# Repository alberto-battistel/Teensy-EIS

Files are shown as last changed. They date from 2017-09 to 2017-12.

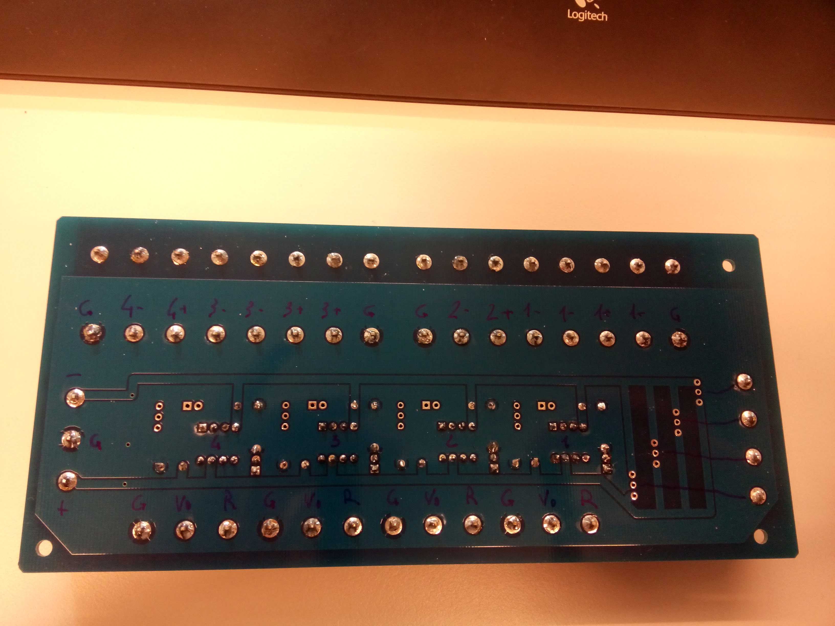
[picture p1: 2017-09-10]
analog front-end/4Input-1Output_board/srDescription_Figures/Board_Backside.jpg

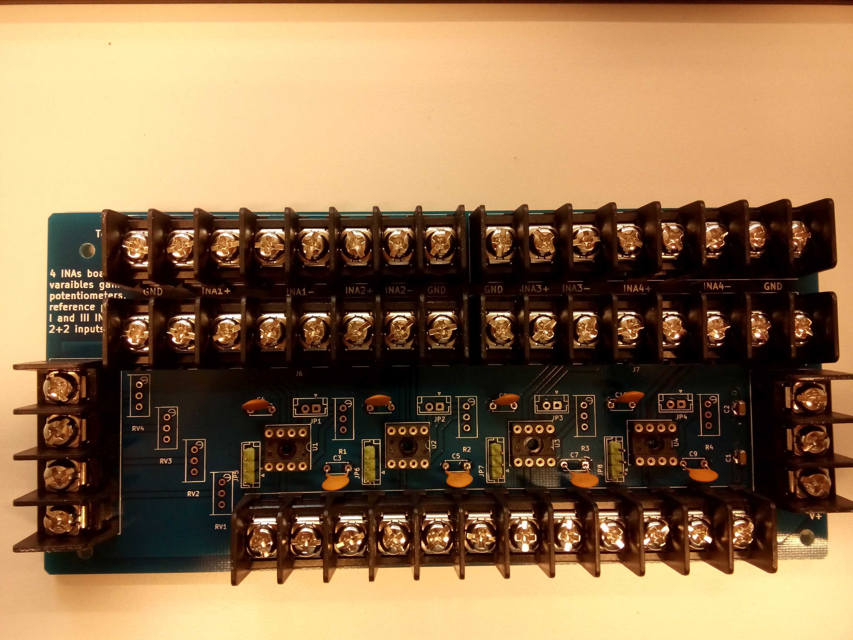
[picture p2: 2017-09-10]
analog front-end/4Input-1Output_board/srDescription_Figures/Board_Frontside.jpg

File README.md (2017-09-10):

# Teensy-EIS

At the moment this git is still slightly chaotic, but it is getting better.
The idea is to use the two ADCs of the Teensy 3.6 (pjrc.com) to aquire data and the DAC to create the perturbation (sinus/multisine) to work as an impedance analyzer. All controlled by a PC using Python, which also make the analysis part. We have an analog front-end for voltage shift (Teensy works 0-3.3V both ADC and DAC) to connect to the real potentiostat. This is tested and works.

## 1 - ADC-DAC
ADC-DAC.ino and readFromPython.py work together. They are THE Teensy-EIS programs. CalculateParameters.m helps to make the parameters to feed in Python.

## 2 - Examples
In ADC-DAC there are examples of the part of the ADC-DAC.ino. DAC is for the DAC and PingPong manages the serial communication with the PC. They are more or less the most updated or the same as in ADC-DAC.ino.

## 3 - Regarding the DAC
The signal for the DAC is generated through a Matlab/GNU Octave/Scilab script. (Generate_DAC_vector). 

## 4 - Analog front-end
In analog front-end there is all about the core of the voltage shift. All the analog interface with the instrument is based on four INA128. They are very flexible pieces. There is no schematic for the power stage and activation of the signal line, but the elements are in the two PDF.

## 5 - Control flow
In Schematics there are the diagrams of the programs. At the moment only the part for the aquisition, which is the most complex. In summary, the Teensy can aquire infinite amount of data which are streamed in blocks to the PC. Python can handle easily several milions data points. 

## 6 - pointer?
pointers-reference-test contains a couple of examples about passing by reference or by pointer to a function. Not fundamental for the rest, just to remember.

------------------------------------
# Version list:

## Version 1.00
Fully operational tidy up version.

## Version 0.99
Fully operational prototype, both for the programing side and for the analog side. 

------------------------------------
# Bug List:
So we can keep track of what needs to be fixed

-To be filled (Priority: 1)

------------------------------------
# Future Feature List:

## Version 1.1?
what shall we implement next?

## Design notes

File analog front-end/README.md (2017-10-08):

# Analog front-end
The analog front-end interfaces the *Teensy* to the instrument (potentiostat). It serves as conditioning of the signals. It mainly provides low impedance for the inputs, level shift (*Teensy* is 0-3.3V), and some degree of rejection for ground loops (still to understand a bit better). It also features an independent power stage (USB compatible) to handle bipolar signals.

## Signal conditioning
At the moment the conditioning is build on 4 **INAs 128** (Instrumentation amplifiers) from Texas Instruments. They are flexible building blocks featuring low noise, low distortion, easy level shift, and high impedance inputs (10 GOhm). Two INAs are used to buffer, level shift, and shrink the DAC (digital to analog converter) of the *Teensy* and the other two are for level shifting of the inputs of the two ADCs (analog to digital converter). 
Analog filtering can be easily attached to the INAs.
**4Input-1Output_board** contains the full design (schematics and printed circuit board layout with bill of components) to build up the signal conditioning part. It is a very flexible board. We also employ it for *additional reference electrode probes* in electrochemical cells or to *break groud loops*.

## Power
The power stage is based on a **DC-DC converter** (*NMA0515SC* from Murata). It takes 5 V as input and provides +/- 15 V. It may be connected to the *Teensy* and take power from the same USB cable, but we did not test this yet. The bipolar voltage is used to power the INAs. The positive rail is also used to hold a normally open **signal relay** (*MT2 Relay* from AXICOM). This relay is controlled by a digital pin of the *Teensy* through a transistor (*2N3904*) and it is necessary to cut the DAC line from the *Teensy* toward the instrument so that unwanted signals cannot be injected (for example when you turn on the *Teensy*...).

## State of the material
At the moment the schematics and the PCB layout signal conditioning part is available in **4Input-1Output_board**, but we may come out with a more practical design later. 
**Complete_analog_front-end.pro** (*KiCAD project* in **Design_schematics**) contains the *functional design* of the project with the fundamental connections between the *Teensy* and the analog front-end and the power stage.

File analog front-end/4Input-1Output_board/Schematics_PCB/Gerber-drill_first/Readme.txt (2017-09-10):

Contact:
Alberto Battistel

Email:
alberto.battistel@epfl.ch

Address:
EPFL Valais Wallis
Laboratoire d’Electrochimie Physique et Analytique (LEPA)
Rue de l'Industrie 17
Case Postale 440
CH-1951 Sion

updated version: 6 February 2017

features
board with 2 copper layer
dimensions: 182.86 mm * 83.82 mm
silkscreen only on top
soldermask on top and bottom

filenames

top silkscreen: schematic3-F.SilkS

top soldermask: schematic3-F.Mask

top copper: schematic3-F.Cu

bottom copper: schematic3-B.Cu

bottom soldermask: schematic3-B.Mask

board outline: schematic3-Edge.Cuts

NC Drill: schematic3.drl

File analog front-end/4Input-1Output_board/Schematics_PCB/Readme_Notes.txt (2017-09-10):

First manufactoring 
6 Feb 2017

Problems:

1- rong footprint for the two 10 uF capacitors. It is possible to solder them but it is annoying.
2- Errors in some writings: board description, INAs inputs.

24 Feb 2017

Corrected:
1- correction of board description and INAs inputs.

To do:
correct footprint of 10 uF capacitors.

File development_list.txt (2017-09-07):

#List of things to implement

## Add license

## Loop microcontroller
activate DAC2 for voltage shift
make functions in the sketch
loop the aquisition for listening from the PC

## Loop python control
Send parameters (Pingpong script)
make analysis (FFT)

## Analog front-end
for DAC (voltage divider, voltage shift, activation relay)
for ADC (voltage shift)
transistor to drive the relay from the Teensy
additional transistors for 5V communication (trigger instrument)

## Real experiment
digital test (impendance DAC vs 2*ADC) to see resolution, linearity
real analog experiment interfaced with a potentiostat

## Future staff
Raspberry PI
portable potentiostat
different experiments (CV, battery cycles)
GUI

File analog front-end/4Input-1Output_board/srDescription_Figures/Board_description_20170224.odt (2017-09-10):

4 INAs board

Alberto Battistel

24 February 2017

This board contains is made to allocate 4 INAs and 4 variable voltage dividers. INA 1 and 3 have two screw terminals for every inputs. INA 2 and 4 have only one screw terminal for input.

Signal inputs Signaloutputs Voltage dividers Power
Figure 1: Top view of the board.

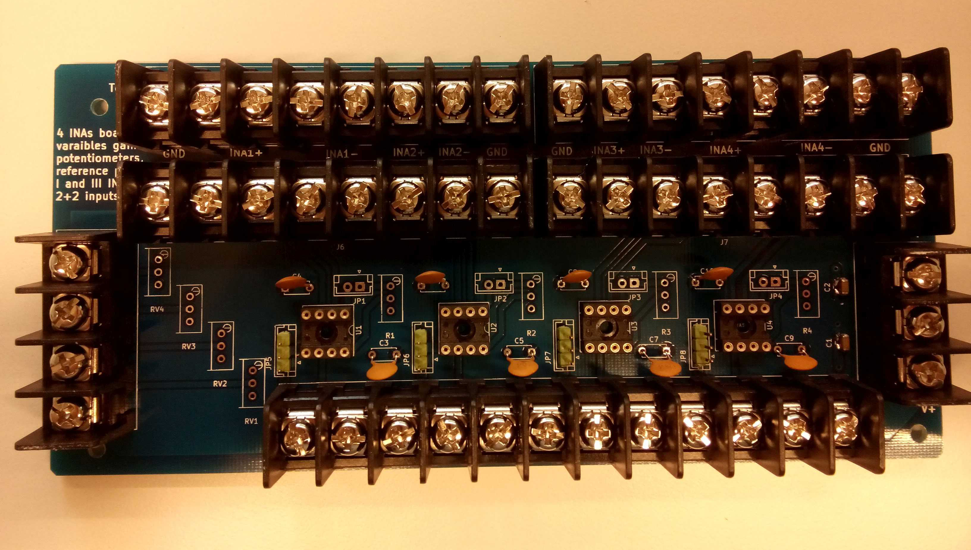
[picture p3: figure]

Note that there are some errors on the labels of the inputs. The backside (Figure 2) has the right labels.

The double terminal row on the signal inputs can be used for filtering and summing.

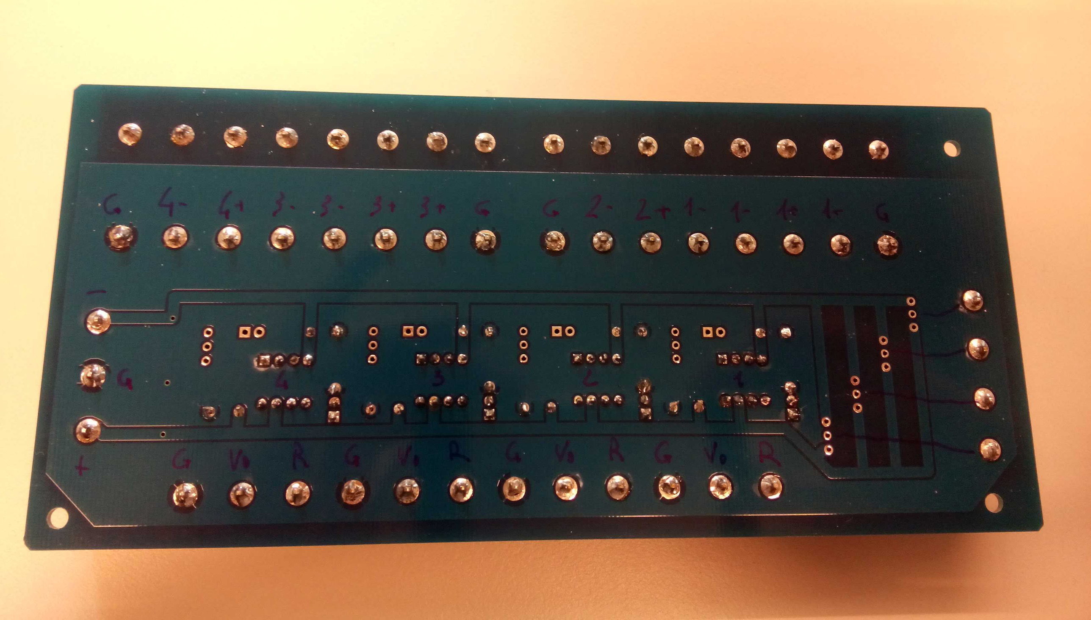
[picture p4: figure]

Figure 2: back side of the board with right labels

Label | Description
G | Ground
R | External reference potential
Vo | INA output
+ | Positive rail
− | Negative rail
n+ | Positive input INA n
n− | Negative input INA n

Table 1: labels on the board.

INAOn the board is possible to change the gain factor through a variable resistance and select if the INA works against ground or against a provided reference voltage.

Variable resistor for gain Jumper for gain Jumper for external Reference potential Refer to ground Refer to external reference
Figure 3: single INA block with jumpers for gain and reference potential.

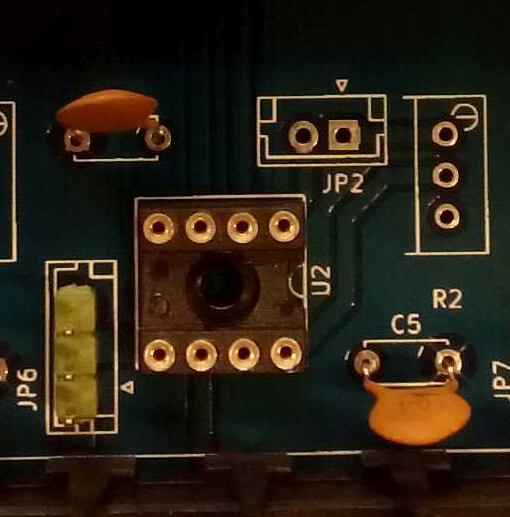
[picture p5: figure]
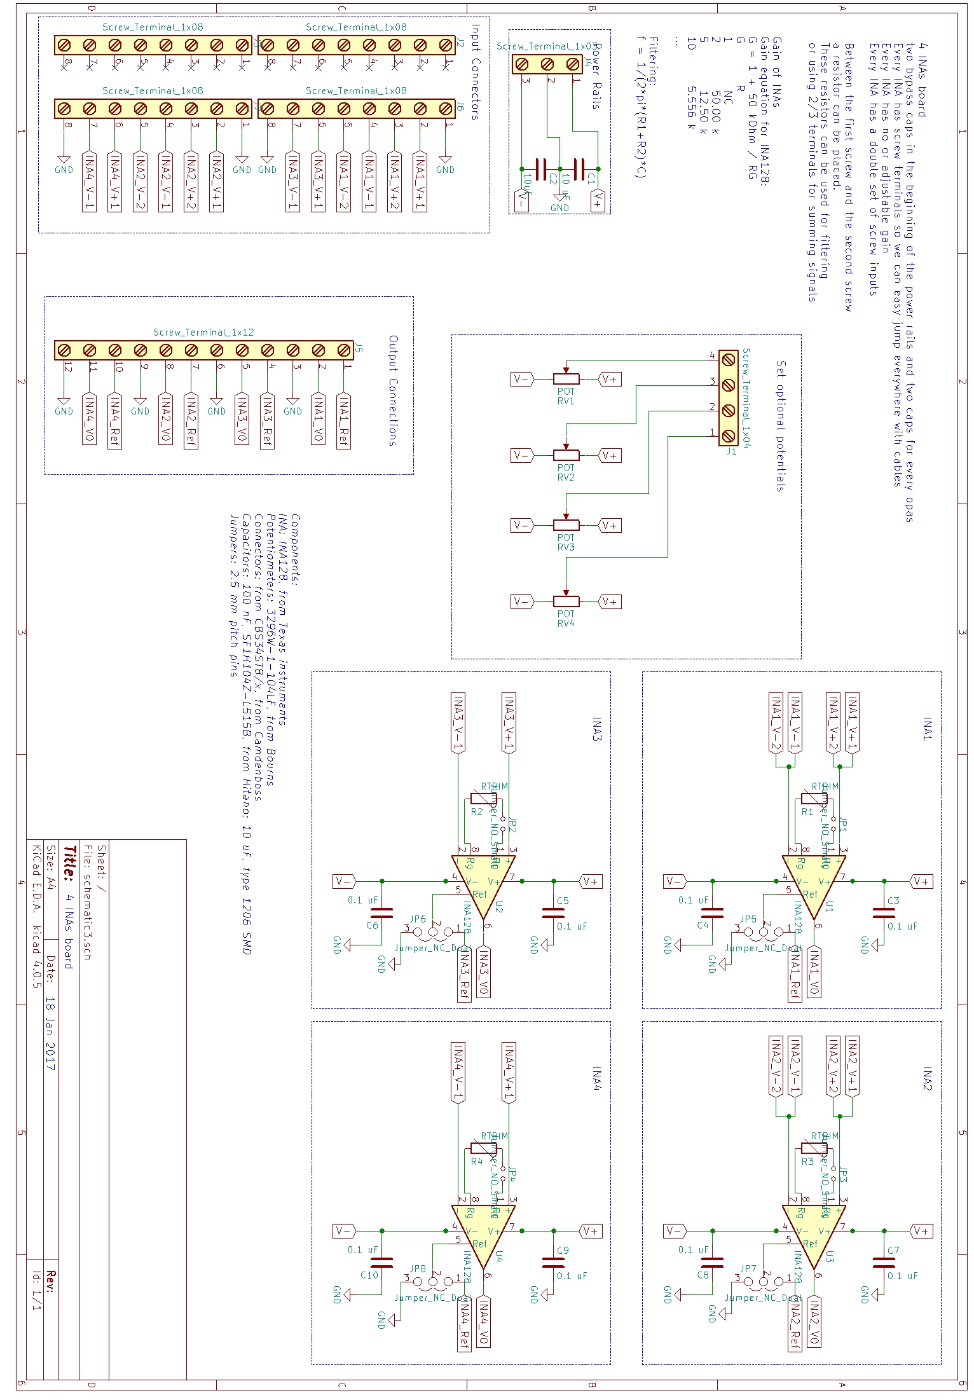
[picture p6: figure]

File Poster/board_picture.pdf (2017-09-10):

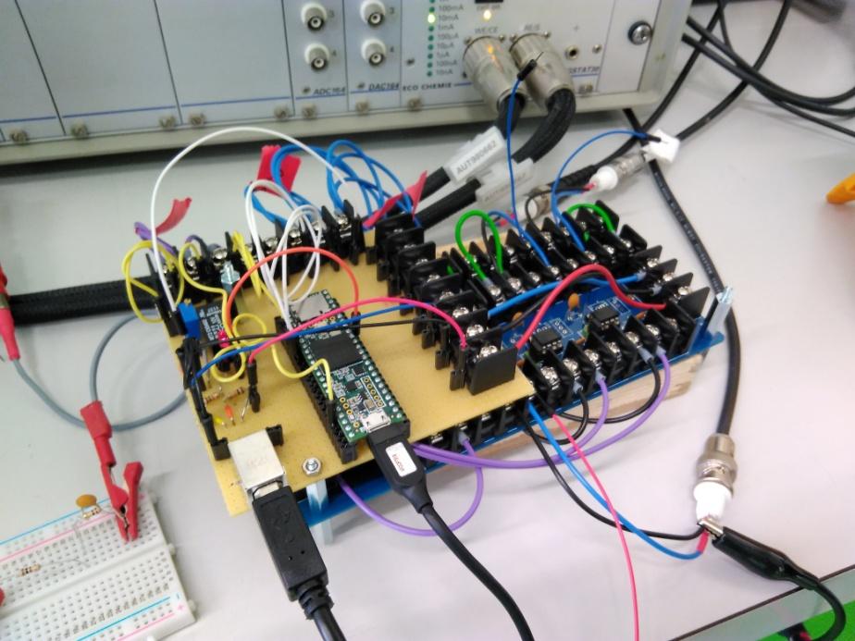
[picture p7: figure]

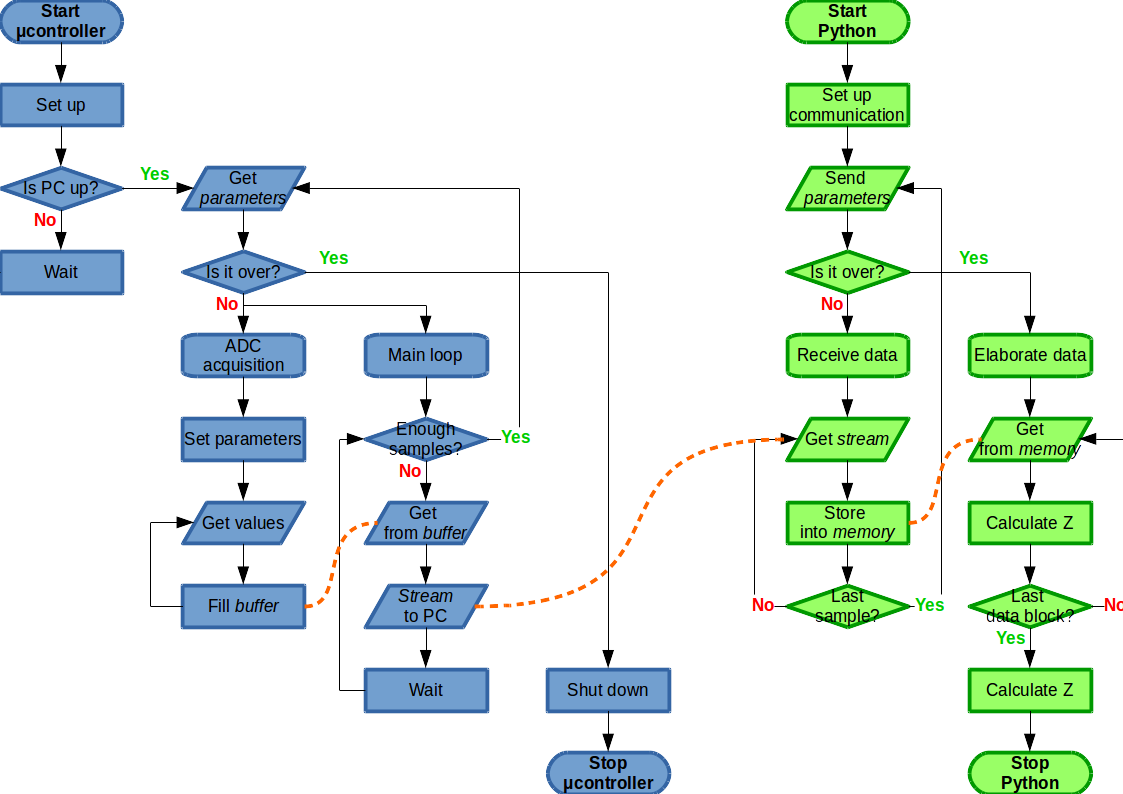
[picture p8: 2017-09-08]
Schematics/FlowChartProgram.png

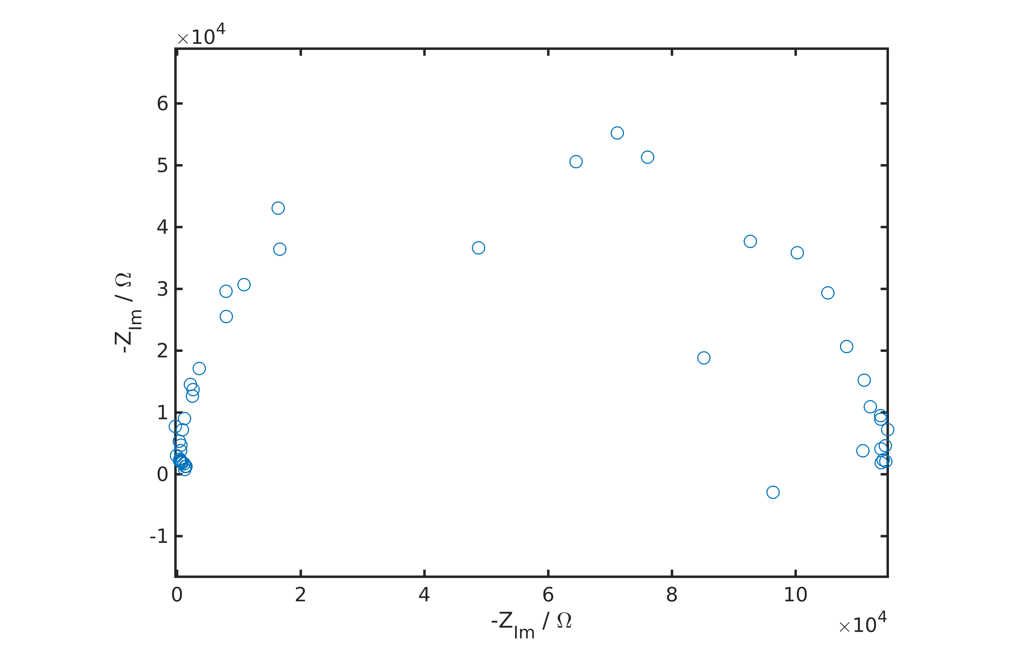
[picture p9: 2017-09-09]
Poster/GoodNyquist.png

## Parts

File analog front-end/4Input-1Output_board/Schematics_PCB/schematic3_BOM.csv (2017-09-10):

Id | Designator | Package | Quantity | Designation | Supplier and ref
1 | J7,J6,J3,J2 | Camdenboss_Screw_terminal_8x9.5mm | 4 | Screw_Terminal_1x08
2 | J4 | Camdenboss_Screw_terminal_3x9.5mm | 1 | Screw_Terminal_1x03
3 | C1 | C_0603_HandSoldering | 1 | 10 uF
4 | C2 | C_0603_HandSoldering | 1 | 10uF
5 | U1,U2,U3,U4 | DIP-8_W7.62mm_Socket | 4 | INA128
6 | J5 | Camdenboss_Screw_terminal_12x9.5mm | 1 | Screw_Terminal_1x12
7 | J1 | Camdenboss_Screw_terminal_4x9.5mm | 1 | Screw_Terminal_1x04
8 | C3,C4,C5,C6,C7,C8,C9,C10 | C_Disc_D5.0mm_W2.5mm_P5.00mm | 8 | 0.1 uF
9 | R1,R2,R3,R4 | Potentiometer_Bourns_3296W_3-8Zoll_Inline_ScrewUp | 4 | RTRIM
10 | RV1,RV2,RV3,RV4 | Potentiometer_Bourns_3296W_3-8Zoll_Inline_ScrewUp | 4 | POT
11 | JP1,JP2,JP3,JP4 | JST_EH_B02B-EH-A_02x2.50mm_Straight | 4 | Jumper_NO_Small
12 | JP5,JP6,JP7,JP8 | JST_EH_B03B-EH-A_03x2.50mm_Straight | 4 | Jumper_NC_Dual

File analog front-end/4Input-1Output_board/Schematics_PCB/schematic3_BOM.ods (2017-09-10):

Id | Designator | Package | Quantity | Designation | Supplier and ref
1 | J7,J6,J3,J2 | Camdenboss_Screw_terminal_8x9.5mm | 4 | Screw_Terminal_1x08
2 | J4 | Camdenboss_Screw_terminal_3x9.5mm | 1 | Screw_Terminal_1x03
3 | C1 | C_0603_HandSoldering | 1 | 10 uF
4 | C2 | C_0603_HandSoldering | 1 | 10uF
5 | U1,U2,U3,U4 | DIP-8_W7.62mm_Socket | 4 | INA128
6 | J5 | Camdenboss_Screw_terminal_12x9.5mm | 1 | Screw_Terminal_1x12
7 | J1 | Camdenboss_Screw_terminal_4x9.5mm | 1 | Screw_Terminal_1x04
8 | C3,C4,C5,C6,C7,C8,C9,C10 | C_Disc_D5.0mm_W2.5mm_P5.00mm | 8 | 0.1 uF
9 | R1,R2,R3,R4 | Potentiometer_Bourns_3296W_3-8Zoll_Inline_ScrewUp | 4 | RTRIM
10 | RV1,RV2,RV3,RV4 | Potentiometer_Bourns_3296W_3-8Zoll_Inline_ScrewUp | 4 | POT
11 | JP1,JP2,JP3,JP4 | JST_EH_B02B-EH-A_02x2.50mm_Straight | 4 | Jumper_NO_Small
12 | JP5,JP6,JP7,JP8 | JST_EH_B03B-EH-A_03x2.50mm_Straight | 4 | Jumper_NC_Dual
 | Description | Reference | Distrelec Art.Nr. | Type | Price / CHF | Quantity | total cost / CHF
 | potentiometers | Potentiometer_Bourns_3296W_3-8Zoll_Inline_ScrewUp | 164-00-721 | 3296W-1-104LF | 1.9 | 20 | 38
 | screw terminals | Camdenboss_Screw_terminal_3x9.5mm | 148-31-248 | CBS34ST8/3 | 1.1 | 10 | 11
 |  | Camdenboss_Screw_terminal_4x9.5mm | 148-31-249 | CBS34ST8/4 | 1.52 | 10 | 15.2
 |  | Camdenboss_Screw_terminal_8x9.5mm | 148-31-254 | CBS34ST8/8 | 2.8 | 20 | 56
 |  | Camdenboss_Screw_terminal_12x9.5mm | 148-31-258 | CBS34ST8/12 | 3.75 | 10 | 37.5
 | capacitors | C_Disc_D5.0mm_W2.5mm_P5.00mm | 165-65-659 | SF1H104Z-L515B | 0.1044 | 100 | 10.44
 |  | C_0603_HandSoldering | 300-66-117 | RND 1501206X106K250 | 0.1004 | 20 | 2.008
 | pins |  |  |  |  |  | 0
 | jumpers | jumpers | 124-50-887 | CAB4GS | 0.136 | 50 | 6.8
 |  |  |  |  |  |  | 176.948
 | Description | Distrelec Art.Nr. | Type | Price / CHF | Quantity | total cost / CHF
 | potentiometers | 164-00-721 | 3296W-1-104LF | 1.9 | 20 | 38
 | screw terminals | 148-31-248 | CBS34ST8/3 | 1.1 | 10 | 11
 |  | 148-31-249 | CBS34ST8/4 | 1.52 | 10 | 15.2
 |  | 148-31-254 | CBS34ST8/8 | 2.8 | 20 | 56
 |  | 148-31-258 | CBS34ST8/12 | 3.75 | 10 | 37.5
 | capacitors | 165-65-659 | SF1H104Z-L515B | 0.1044 | 100 | 10.44
 |  | 300-66-117 | RND 1501206X106K250 | 0.1004 | 20 | 2.008
 | jumpers | 124-50-887 | CAB4GS | 0.136 | 50 | 6.8

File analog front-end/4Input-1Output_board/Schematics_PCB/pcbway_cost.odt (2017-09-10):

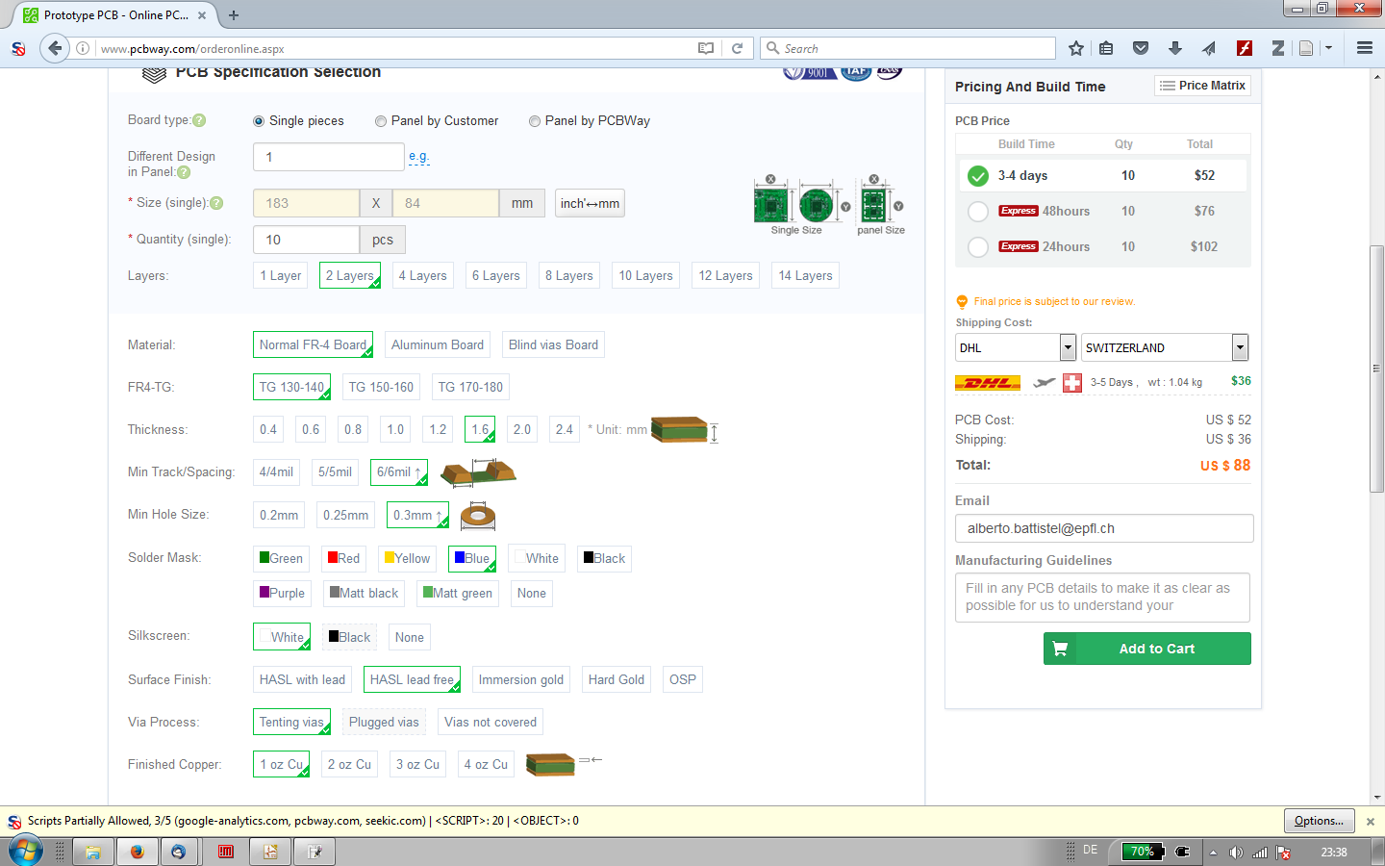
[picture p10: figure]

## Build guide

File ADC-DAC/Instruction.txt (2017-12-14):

every time you shutdown Teensy (exit(0)), you need to press the botton on the Teensy.

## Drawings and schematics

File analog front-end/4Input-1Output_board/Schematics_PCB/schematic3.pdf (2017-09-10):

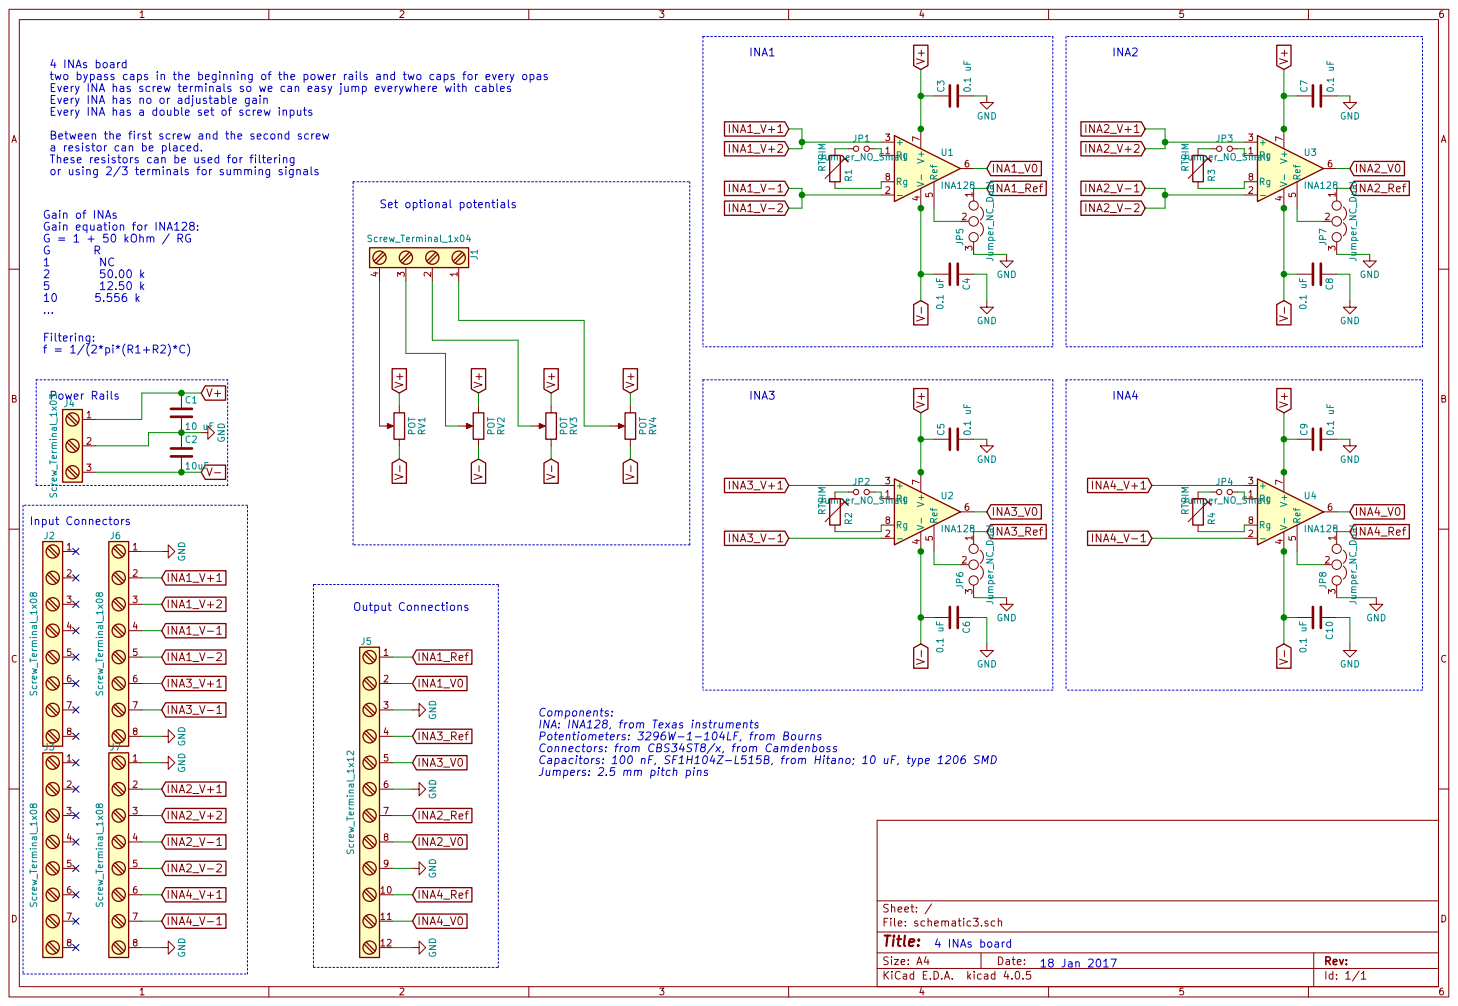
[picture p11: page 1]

4 INAs board
two bypass caps in the beginning of the power rails and two caps for every opas
Every INA has screw terminals so we can easy jump everywhere with cables
Every INA has no or adjustable gain
Every INA has a double set of screw inputs Between the first screw and the second screw

These resistors can be used for filtering

a resistor can be placed.

J5 Screw_Terminal_1x12
INA4_V0 GND GND GND GND

INA: INA128, from Texas instruments
Potentiometers: 3296W-1-104LF, from Bourns
Connectors: from CBS34ST8/x, from Camdenboss
Capacitors: 100 nF, SF1H104Z-L515B, from Hitano; 10 uF, type 1206 SMD
Jumpers: 2.5 mm pitch pins

Id: 1/1 Title: File: schematic3.sch Sheet: /

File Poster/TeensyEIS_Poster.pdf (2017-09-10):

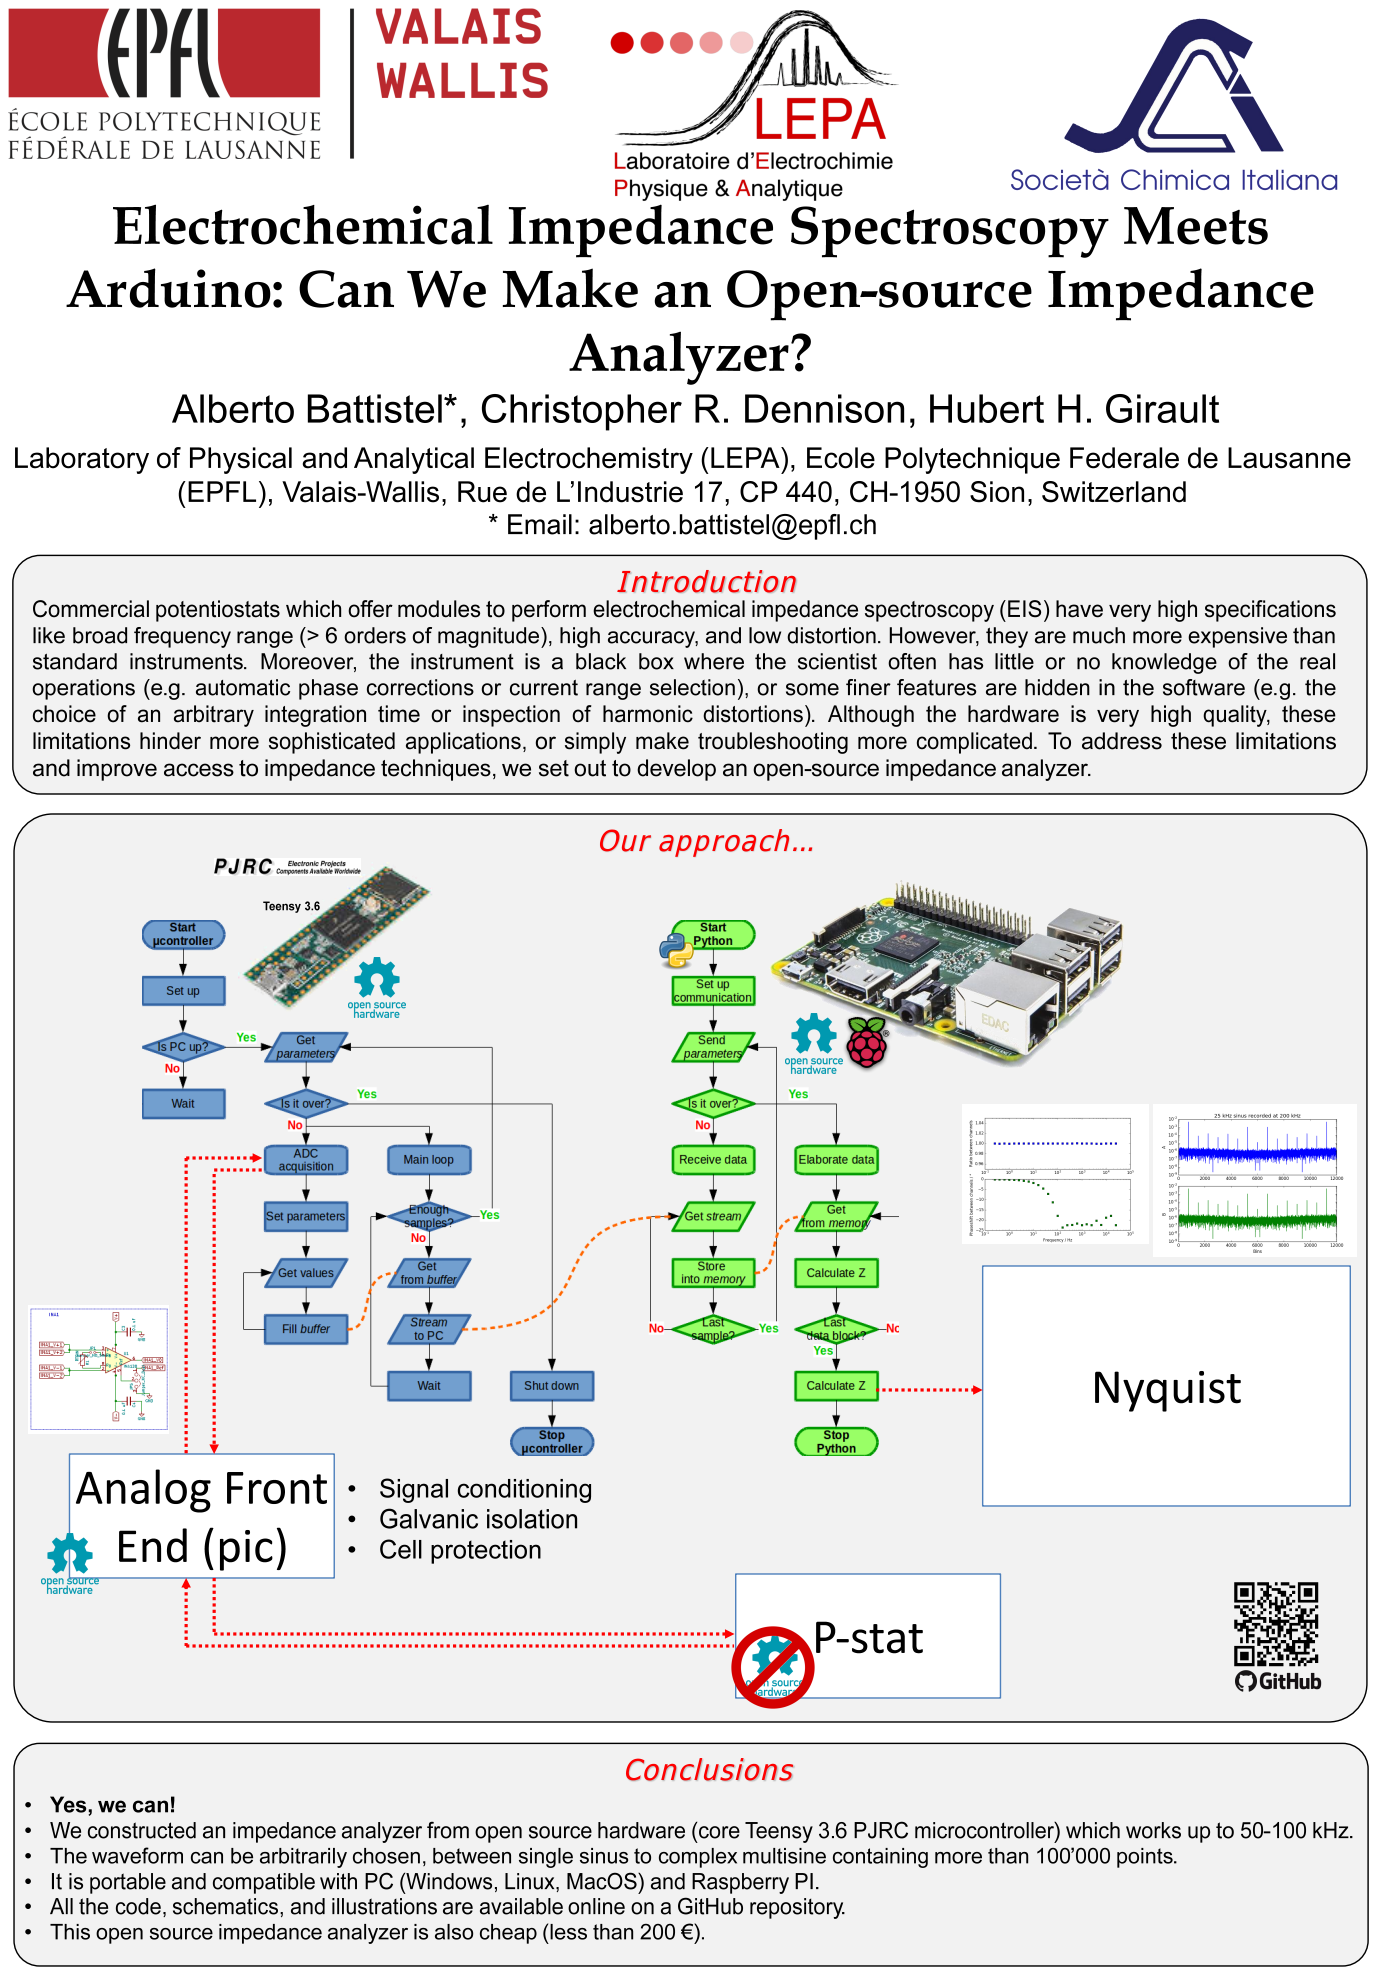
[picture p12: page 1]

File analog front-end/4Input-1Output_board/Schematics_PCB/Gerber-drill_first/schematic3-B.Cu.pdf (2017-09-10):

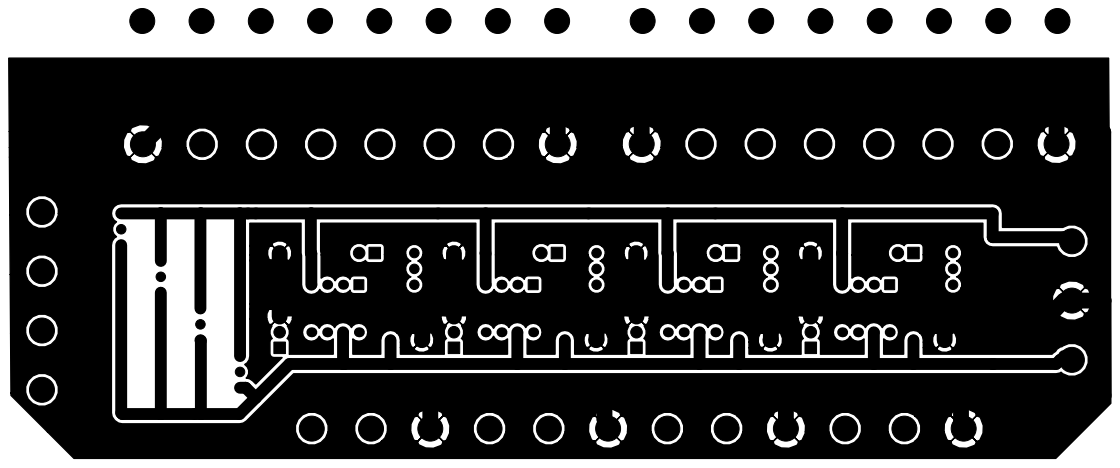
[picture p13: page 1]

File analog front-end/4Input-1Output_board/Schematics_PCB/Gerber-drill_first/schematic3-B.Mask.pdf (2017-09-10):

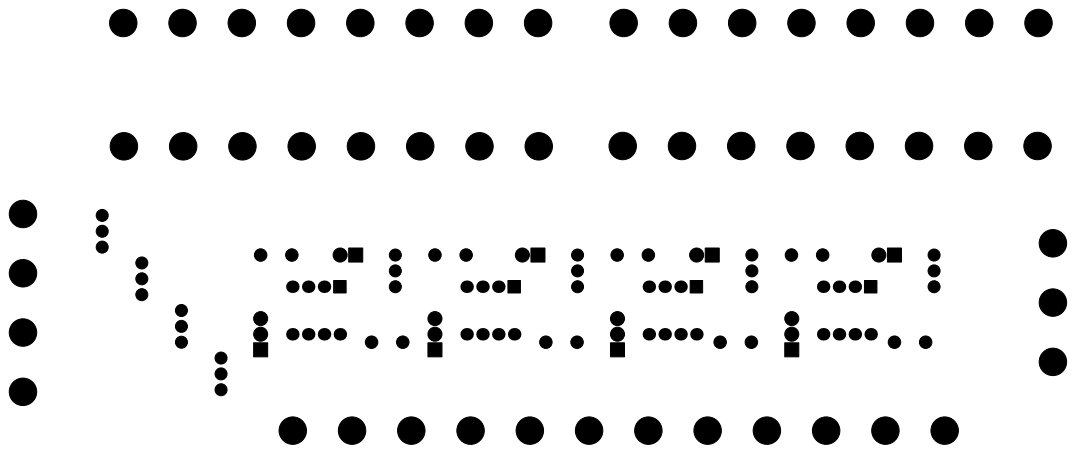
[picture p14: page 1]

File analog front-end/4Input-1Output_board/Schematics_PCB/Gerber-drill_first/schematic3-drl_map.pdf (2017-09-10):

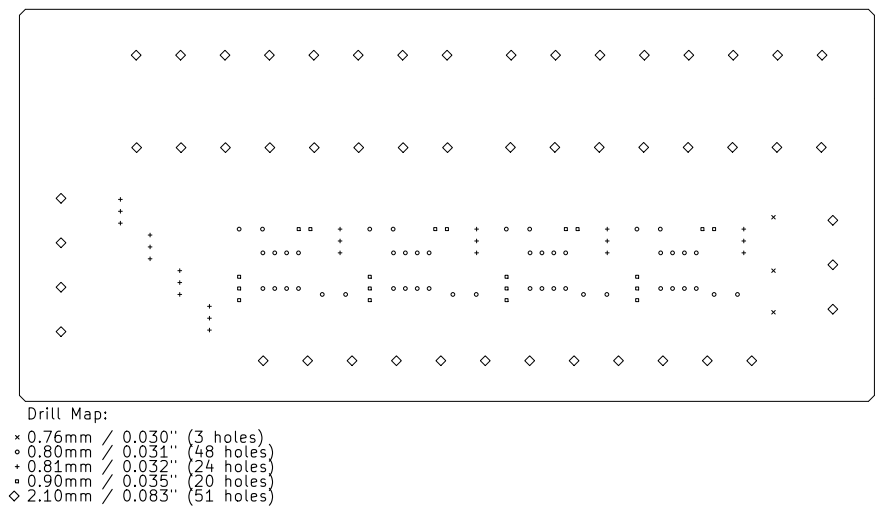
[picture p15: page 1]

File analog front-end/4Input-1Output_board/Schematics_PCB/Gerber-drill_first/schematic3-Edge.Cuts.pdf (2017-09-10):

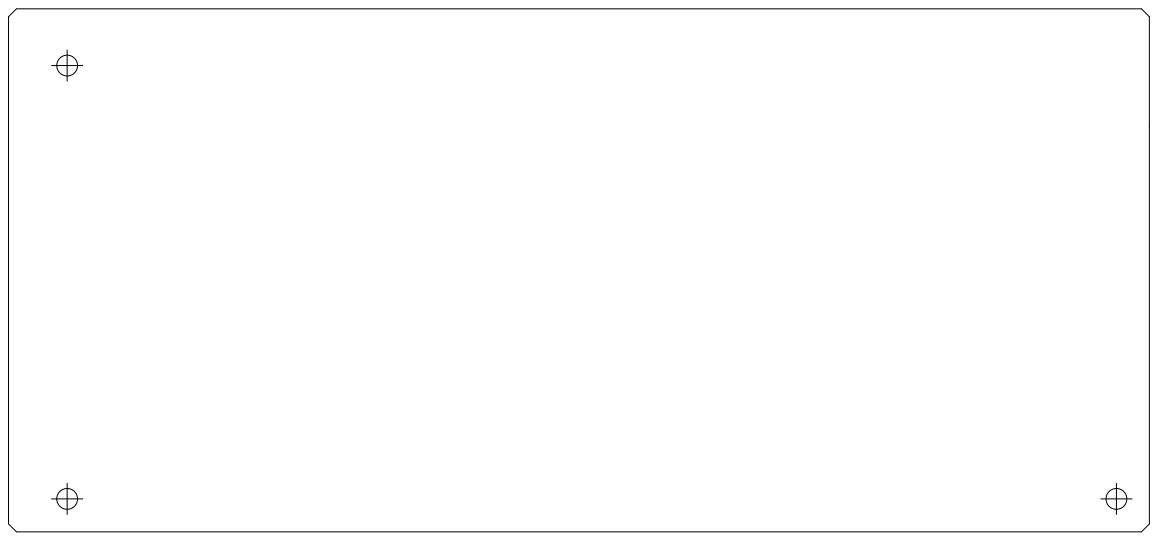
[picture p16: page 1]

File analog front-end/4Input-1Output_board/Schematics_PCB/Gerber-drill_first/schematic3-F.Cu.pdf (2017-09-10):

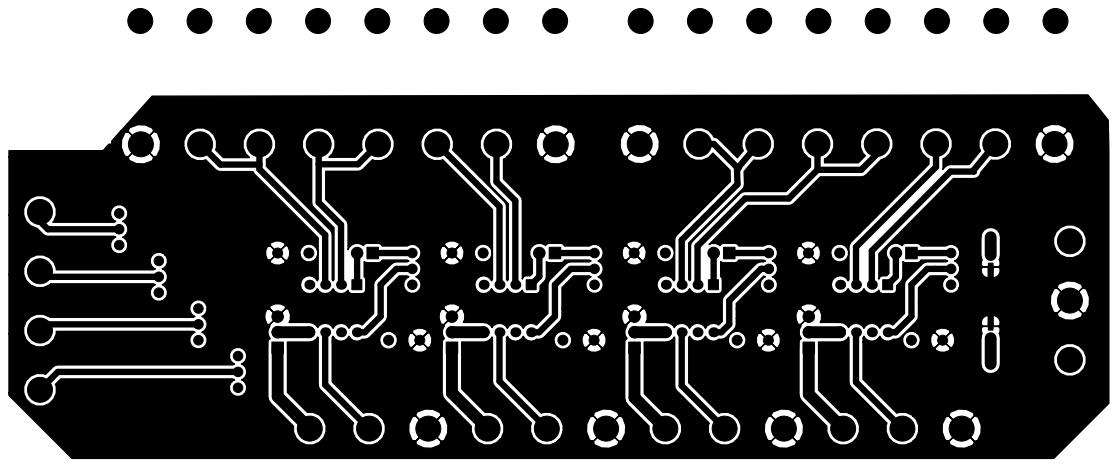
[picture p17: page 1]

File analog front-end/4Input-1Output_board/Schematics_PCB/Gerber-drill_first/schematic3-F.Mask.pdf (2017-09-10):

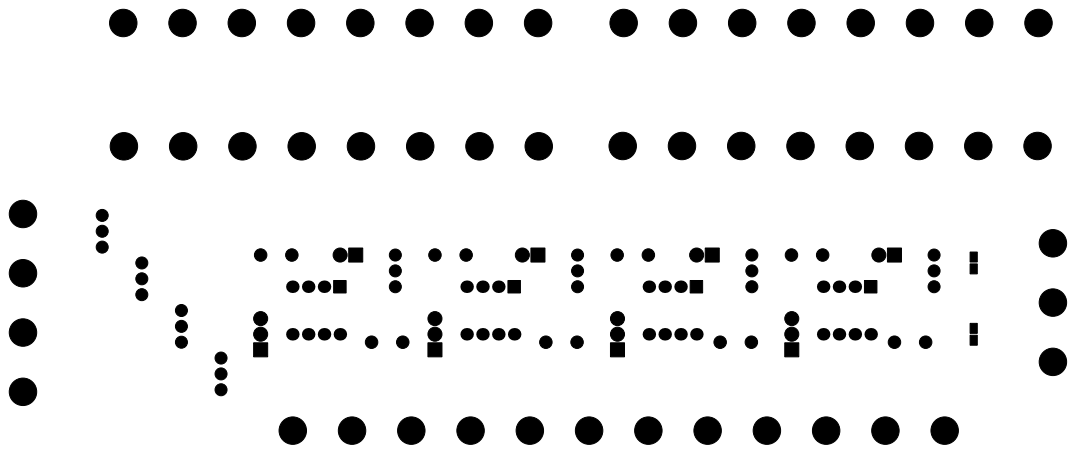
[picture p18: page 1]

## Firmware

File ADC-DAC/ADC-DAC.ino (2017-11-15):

#include <ADC.h>
#include <DMAChannel.h>
#include <array>
#include "DefaultParameters.h"
#include "DAC.h"


/* do you want to check timing?
 *  it print info about how many samples are collected per iteration
 *  and timing...
 */
//#define DEBUG

// ADC pins 
const uint8_t adc_pin0 = A9;  // digital pin 23, on ADC0
const uint8_t adc_pin1 = A19; // digital pin 31, on ADC1
// LED pin
const int ledPin = 13;
// Realy pin
const int RelayPin = 24;

// get parameters from the PC
#include "PingPong.h"   // contains function to get Parameters from Python

/* Count number of samples
 *  allow to stop the stream after collecting maxSamples
 */
bool stop4Samples[2] = {false, false};    // flag, signal that it streamed all the data of channels 0
uint32_t counterSamplesADC0 = 0;        // counter for data streamed for channel 0
uint32_t counterSamplesADC1 = 0;        // counter for data streamed for channel 1

/* Settings for Ring buffer (DMA)  */
// DMA buffer size
#define BUFFERSIZE 4096

// stream buffer size
uint16_t streamBuffer[2][BUFFERSIZE];

/* flags and counter */
// command to stop streaming
boolean streamData = true;

#ifdef DEBUG
// track in print time for serial print
unsigned long time_us = 0;
// count iterations
int16_t Iterations = 0;
#endif

// store index of DMA buffer
volatile size_t buffer_idx0;
volatile size_t buffer_idx1;

// store old index of DMA buffer
volatile size_t old_buffer_idx0 = 0;
volatile size_t old_buffer_idx1 = 0;

// delay between loops to collect a suitable number of data to stream
uint32_t Delay_loop;

/*
 * I did not touch much from here on
 */

ADC adc;
DMAChannel dma0;
DMAChannel dma1;

struct CapturePair {
    uint16_t v_adc0;
    uint16_t v_adc1;
};
std::array<volatile CapturePair, BUFFERSIZE> buffer;
volatile size_t write_pos = 0;

/*  
 *  Function for modifing and running ADC and DAC
 */
#include "SettingParameters.h"


/*
 * Setup
 */

void setup() {
    pinMode(ledPin, OUTPUT);
    pinMode(RelayPin, OUTPUT);
    Serial.begin(9600);
    while (!Serial) {
    ; // wait for serial port to connect.
    }

    // DAC
    analogWriteResolution(12);
    pinMode(pinDAC, OUTPUT);
    pinMode(pinREF, OUTPUT);
    DACvoltageReference();

    // ADC
    pinMode(adc_pin0, INPUT);
    pinMode(adc_pin1, INPUT);
    activateADC();
    
    // wait for input
    #ifdef DEBUG
    Serial.println("Bebugging is on!");
    #endif

    Serial.println("Ready!");
    delay(500);
    while (!(Serial.available() > 0))  {
        digitalWrite(ledPin, HIGH);   // set the LED off
        Serial.println("Waiting...");
        Serial.send_now();
        delay(250);
        digitalWrite(ledPin, LOW);   // set the LED off
        delay(250);
    }
}


/*
 * loop
 */
void loop() {
    switch (Parameters.StartStop) {
        case 2: {
            shutDown();
            //exit(0);
            break;
        }
        case 1: {
            // get parameters from the pc
            digitalWrite(ledPin, LOW);   // set the LED off
            while (Parameters.StartStop == 1) pingPongParameters();

            digitalWrite(ledPin, HIGH);   // set the LED on
            digitalWrite(RelayPin, HIGH);
            delayMicroseconds(100000);
            
            // start everything
            // DAC
            timerDAC.begin(DAC_callback, Parameters.DAC_delay);
            
            // set ADC average and resolution
            setADC(Parameters.ADC_average, Parameters.ADC_resolution);
            
            // calculate how much delay in the loop
            Delay_loop =  calculateDelay_loop(Parameters.ADC_frequency);
            
            // enable PDB
            setPDB(Parameters.ADC_frequency);
            
            // Kick off ADC conversion.
            startConversion();
            
            // restart counting of samples
            counterSamplesADC0 = 0;
            counterSamplesADC1 = 0;
            
            // restart index of DMA buffer
            old_buffer_idx0 = 0;
            old_buffer_idx1 = 0;

            // flag 
            Parameters.ADC_enoughSamples[0] = false;
            Parameters.ADC_enoughSamples[1] = false;
           
            Serial.println("Go!");
            
            delayMicroseconds(Delay_loop);
        }      
        default:  {
            // Read position on DMA buffer
            noInterrupts();
            buffer_idx0 = (((uint16_t*) dma0.destinationAddress()) - &buffer[0].v_adc0) / 2;
            buffer_idx1 = (((uint16_t*) dma1.destinationAddress()) - &buffer[0].v_adc1) / 2;
            interrupts();

            #ifdef DEBUG
            // count iterations and tell when an ADC finishes
            if (Parameters.ADC_enoughSamples[0]) Serial.println("ADC0 Done!");
            if (Parameters.ADC_enoughSamples[1]) Serial.println("ADC1 Done!");
            Serial.print("Iteration: ");
            Serial.println(Iterations++);      
            #endif
        }
    }

    // number of values streamed
    uint16_t nvalues0;
    uint16_t nvalues1;
    
    #ifdef DEBUG
    // update timer
    time_us = micros();
    #endif

    // Transfer from ringbuffer (DMA) to stream buffer and stream
    if(streamData) { // do it only if
    nvalues0 = StreamData(counterSamplesADC0, 0, &buffer[0].v_adc0, old_buffer_idx0, buffer_idx0);
    counterSamplesADC0 = counterSamplesADC0 + (uint32_t)nvalues0;

    nvalues1 = StreamData(counterSamplesADC1, 1, &buffer[0].v_adc1, old_buffer_idx1, buffer_idx1);
    counterSamplesADC1 = counterSamplesADC1 + (uint32_t)nvalues1;
    }

    #ifdef DEBUG
    printAllInfo();
    #endif
  
    // get last position in the ring buffer
    old_buffer_idx0 = buffer_idx0;
    old_buffer_idx1 = buffer_idx1;

    // no idea, it was here already
    if(adc.adc0->fail_flag || adc.adc1->fail_flag) {
        Serial.println("ADC error in the loop");
        adc.adc0->printError();
        adc.adc1->printError();
    }

    /* Delay the next iteration
     *  it is used to have a good number of samples streamed (ideally 50)
     */
    delayMicroseconds(Delay_loop);
}

// all functions are defined in .h files
// I know it is not the good way, but I could not make work .cpp files...

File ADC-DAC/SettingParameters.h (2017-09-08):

#ifndef SETTINGPARAMETERS_H
#define SETTINGPARAMETERS_H

#include <Arduino.h>
#include <ADC.h>
#include <DMAChannel.h>
#include <array>

/*
 * Function declaration for streaming data and setting the ADC/DAC
 */


/* Calculate the best delay
	 *  it calculates the best delay (Delay_us) between iterations
	 *  to have the best number of samples to send (BEST_N_VAL)
	 *  according to the time it takes to send a value (TIME_1VAL) and the aquistion frequency (FREQUENCY)
	 *  TIME_1VAL is between 1 and 3 us
	 */
uint32_t calculateDelay_loop(float ADC_frequency){
	 #define BEST_N_VAL 100
	 #define TIME_1VAL 3e-6   // s
	 uint32_t Delay_ = max((int32_t)(BEST_N_VAL*(1-TIME_1VAL*Parameters.ADC_frequency)/Parameters.ADC_frequency*1e6), 0);    // us
   Delay_ = min(Delay_, (uint32_t)100000);  // max 900 ms of delay
	 return Delay_;
}

/*  Set PDB stuff
 * 
 */
 void setPDB(float ADC_frequency)  {
    // enable PDB
    // this is part is completely obscure to me...
    SIM_SCGC6 |= SIM_SCGC6_PDB;
    uint32_t mod = (F_BUS / Parameters.ADC_frequency);   // PDB frequency
    //Serial.println(F_BUS / Parameters.ADC_frequency);
    //Serial.println(mod);
    //assert(mod <= 0x10000);
    //Serial.println(PDB0_MOD);
    PDB0_MOD = (uint16_t)(mod-1);
    //PDB0_MOD = (uint32_t)(mod-1);
    //Serial.println(PDB0_MOD);
    PDB0_CH0C1 = PDB_CHnC1_TOS_1 | PDB_CHnC1_EN_1; // PDB triggers ADC0 SC1A
    PDB0_CH1C1 = PDB_CHnC1_TOS_1 | PDB_CHnC1_EN_1; // PDB triggers ADC1 SC1A
    PDB0_SC = ADC_PDB_CONFIG | PDB_SC_PRESCALER(0) | PDB_SC_MULT(0) | PDB_SC_LDOK;
}

/*  Start conversion for ADC DMA stuff
 * 
 */
void startConversion()  {
    PDB0_SC = ADC_PDB_CONFIG | PDB_SC_PRESCALER(0) | PDB_SC_MULT(0) | PDB_SC_SWTRIG; // start
    digitalWrite(ledPin, HIGH);   // set the LED on
}



/*  set ADC parameters
 *  average, resoltution
 */
 void setADC(int8_t ADC_average, int8_t ADC_resolution) {
      /* Settings for ADC
     *  AVERAGE 32 OK at 10 kHz
     *  AVERAGE max 8 at 50 kHz
     *  RESOLUTION 16 at 10 kHz gives a floor noise of almost 0.01 mV
     *  RESOLUTION 12 at 10 kHz gives a floor noise better than 0.1 mV
     *  RESOLUTION 8 at 250 kHz gives a floor noise of 0.1 mV
     */
    adc.setAveraging(ADC_average);
    adc.setResolution(ADC_resolution);

    adc.setConversionSpeed(ADC_CONVERSION_SPEED::VERY_HIGH_SPEED);
    adc.setSamplingSpeed(ADC_SAMPLING_SPEED::VERY_HIGH_SPEED);

    adc.setAveraging(ADC_average, ADC_1); // set number of averages
    adc.setResolution(ADC_resolution, ADC_1); // set bits of resolution

    adc.setConversionSpeed(ADC_CONVERSION_SPEED::VERY_HIGH_SPEED, ADC_1); // change the conversion speed
    adc.setSamplingSpeed(ADC_SAMPLING_SPEED::VERY_HIGH_SPEED, ADC_1); // change the sampling speed

//    adc.adc0->analogRead(adc_pin0); // performs various ADC setup stuff
//    adc.adc1->analogRead(adc_pin1); // performs various ADC setup stuff

    if(adc.adc0->fail_flag || adc.adc1->fail_flag) {
        Serial.println("In setADC:");
        adc.adc0->printError();
        adc.adc1->printError();
    
        //Serial.printf("ADC error, ADC0: %x ADC1: %x\n", adc.adc0->fail_flag, adc.adc1->fail_flag);
    }

    adc.adc0->stopPDB();
    adc.adc1->stopPDB(); 

    // DMA
    dma0.source((uint16_t&) ADC0_RA); // ADC result register
    //dma0.source(ADC0_RA); // ADC result register
    dma0.triggerAtHardwareEvent(DMAMUX_SOURCE_ADC0);
    dma0.destinationBuffer(&buffer[0].v_adc0, buffer.size() * sizeof(buffer[0]));
    dma0.TCD->DOFF = 4;
    dma0.TCD->CITER = buffer.size();
    dma0.TCD->BITER = buffer.size();
    dma0.enable();
    adc.enableDMA(ADC_0);

    dma1.source((uint16_t&) ADC1_RA); // ADC result register
    //dma1.source(ADC1_RA); // ADC result register
    dma1.triggerAtHardwareEvent(DMAMUX_SOURCE_ADC1);
    dma1.destinationBuffer(&buffer[0].v_adc1, buffer.size() * sizeof(buffer[0]));
    dma1.TCD->DOFF = 4;
    dma1.TCD->CITER = buffer.size();
    dma1.TCD->BITER = buffer.size();
    dma1.enable();
    adc.enableDMA(ADC_1);

    adc.adc0->setHardwareTrigger();
    adc.adc1->setHardwareTrigger();
    
}

/*  Activate ADC
 *  it needs to run only once
 */

void activateADC()  {
    adc.adc0->analogRead(adc_pin0); // performs various ADC setup stuff
    adc.adc1->analogRead(adc_pin1); // performs various ADC setup stuff
}

/* Stream data
 *  Transfer from ringbuffer (DMA) to stream buffer and stream
 *  return the number of data streamed
 *  ring buffer can wrap
 *  stream buffer is alway filled from the first position and does not wrap
 */
 uint16_t StreamData(uint32_t NumberOfSamples, uint8_t bufferIndex, volatile uint16_t* DMAbufferAddress, volatile size_t old_buffer_, volatile size_t buffer_) {
    // number of values to stream
    uint32_t nvalues = 0;
    // position in the stream buffer
    uint16_t posStreamBuffer = 0;

    /* first check that the last position and the new position in the DMA buffer are not the same
    * it happens when you start
    */
    if(old_buffer_ != buffer_) {
    /* CASE I
     *  ring buffer did not wrap
     *  no problem data are in the right consecutive order
     */
        if(old_buffer_ < buffer_) {
        // consecutive order
            for(size_t i = old_buffer_; i < buffer_; i++) {
                streamBuffer[bufferIndex][posStreamBuffer++] = *(DMAbufferAddress + i*sizeof(buffer[0].v_adc0));
                nvalues++;
            }
    }
    /* CASE II
     *  ring buffer wrapped
     *  take data from old position until the end of the buffer and start over from the beginning
     */
        else {
            for(size_t i = old_buffer_; i < BUFFERSIZE; i++) {
                streamBuffer[bufferIndex][posStreamBuffer++] = *(DMAbufferAddress + i*sizeof(buffer[0].v_adc0));
                nvalues++;
            }
            for(size_t i = 0; i < buffer_; i++) {
                streamBuffer[bufferIndex][posStreamBuffer++] = *(DMAbufferAddress + i*sizeof(buffer[0].v_adc0));
                nvalues++;
            }
        }
    }

    /* Stream data of the stream buffer
    *  this buffer was filled from the first position
    *  so stream only the right number of values
    *  to improve performances use "Serial" as USB type for teensy (very important)
    *    rise CPU clock
    *    write bytes (1.3 us per data)
    */
    uint16_t last2Stream = posStreamBuffer;
    if(NumberOfSamples+nvalues >= Parameters.ADC_nSamples)  {
  // it is reaching the right number of samples to stream
    uint32_t samplesTooMuch = NumberOfSamples + nvalues - Parameters.ADC_nSamples;
    last2Stream = posStreamBuffer - (uint16_t)samplesTooMuch;
    Parameters.ADC_enoughSamples[bufferIndex] = true;
    streamData = true;
    }
  
  if (Parameters.ADC_enoughSamples[0] && Parameters.ADC_enoughSamples[1]) {
    // ready to receive new parameters
    Parameters.StartStop = 1;
    }
  
    // Advice how many data are going to be streamed
    //Serial.println(Iterations);   // count iterations
    Serial.println(last2Stream);  // use s.readline() to receive

    // Stream bytes
    for(uint16_t i = 0; i < last2Stream; i++) {
  // stream
    Serial.write(lowByte(streamBuffer[bufferIndex][i]));
    Serial.write(highByte(streamBuffer[bufferIndex][i]));
    /* use
    * data = s.read(x) where x is the number of bytes (16 bits = 2 bytes)
    * np.fromstring(data,dtype = np.uint16)
    * to get the data in python
    */
    }
    return last2Stream;   // number of data streamed
}
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

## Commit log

2017-08-28 ADC-DAC starts to work, teensy streams to python, but I lose synchronization sometimes
2017-09-06 Teensy and Python are looping together! Still very rough, but working.
2017-09-07 python and teensy works together, I made a matlab script to calculate the Paramerters. I have problems with the PDB, I think.
2017-09-07 Teensy and python work together. CalculateParameters.m calculates the parameters. Some frequencies come very nice (ADC 200, 20, 8, and 2 kHz) some less.There are loss of data at low frequencies (belo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
2017-09-08 Many small changes, getting close to a good Nyquist plot. Fingers crossed
2017-09-10 Big cleaning. Add all the material for the analog front-end (INAs board). Version 1.00git add .!
    [schematic3-B.Cu.gbl, schematic3-B.Cu.gbr, schematic3-B.Mask.gbr, schematic3-B.Mask.gbs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]
2017-09-23 Started KiCAD schematics of all the analog part of the Teensy-EIS.
    [Complete_analog_front-end.kicad_pcb, Complete_analog_front-end.sch, file59C63832.sch, file59C655E4.sch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]
2017-10-08 Functional diagram of the project is finished. Few details are missing: pull-down resistor, position of the filter capacitor...
    [ADC_input.sch, Complete_analog_front-end.sch, PowerStage.sch, analog_DAC.sch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]
2017-11-15 Fix shutdown. Now there is a 47 kOhm pulldown resitor and the relayPin goes low.
    [analog_DAC.sch]
2017-11-15 Issue #2: define function to communicate with Teensy. Next it is to implement module.
2017-11-16 Made an example script to see how to communicate with Teensy. There are some problems: I cannot restart Teensy from Python and I need to improve the module handling for debugging easy communications.
2017-11-16 Issue #2, I made an example script to see how to communicate with Teensy. There are some problems: I cannot restart Teensy from Python and I need to improve the module handling for debugging easy com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
2017-12-14 Issue#2: Now Python can find the dev value of Teensy. Still problems when Teensy shutdown. There are some extra python scripts but they do nothing.
